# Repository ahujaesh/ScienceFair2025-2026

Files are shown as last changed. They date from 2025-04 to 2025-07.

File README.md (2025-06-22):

After placing third in the state and not advancing to ISEF, I wanted to build something that would allow me to make it there next year. What I came up with was this project: a DIY low cost bioprinter.

[BOM / Parts List](expenses.csv)

[Todo list / Agenda](plan.md) Note: (This will be replaced with a full instruction manual later, but as I am still iterating and changing the way I want to do this, I have included this file temporarily. This file is my thoughts on what the next steps for this project should be, and detailed info on what I am working on currently.)

[Media/Images](media) Images of the project will be uploaded here as they are taken.

What's happened so far?:

- Researched what bioprinting was to make sure it was the right fit for me  
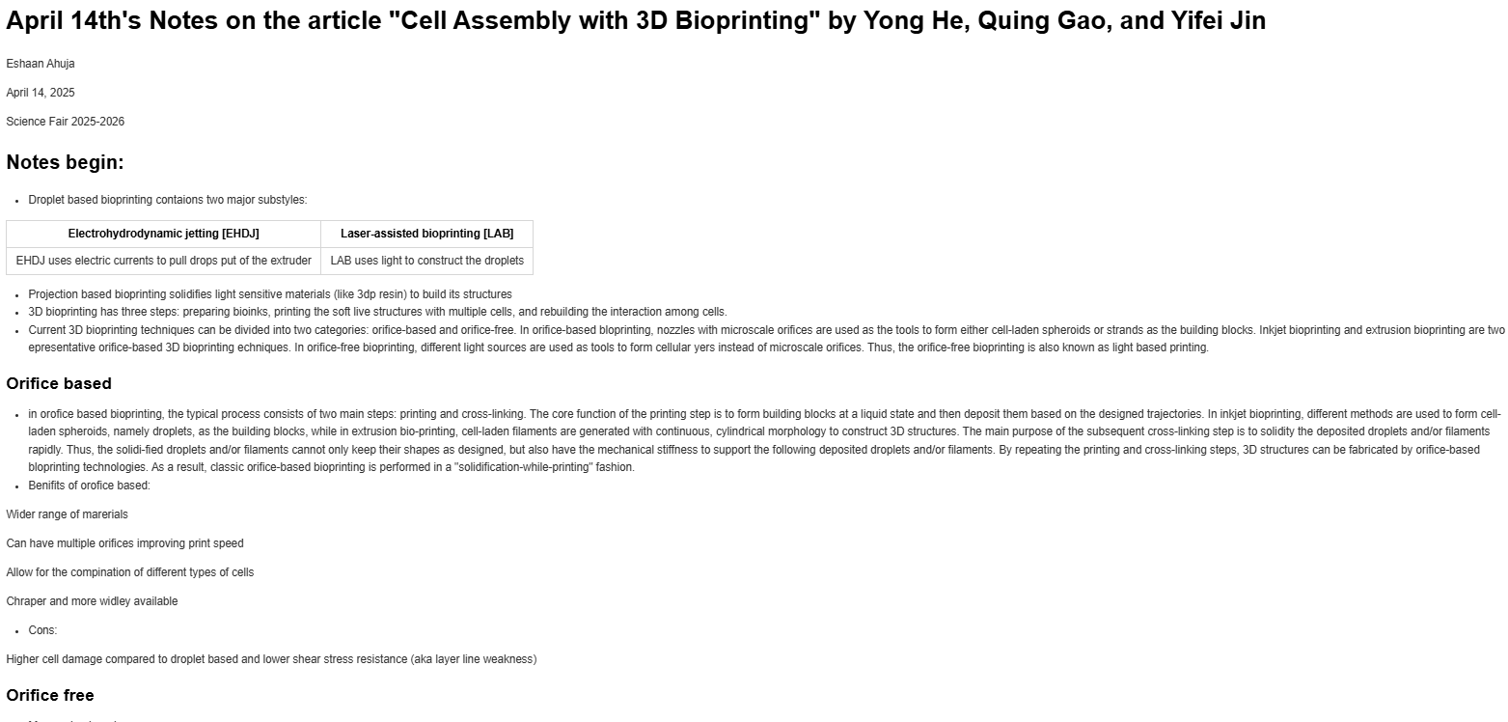
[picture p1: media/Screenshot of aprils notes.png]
Screenshot of notes

- Built an arduino mega based cardboard prototype of a bioprinter alongside a custom gcode interpreter and custom arduino OS  
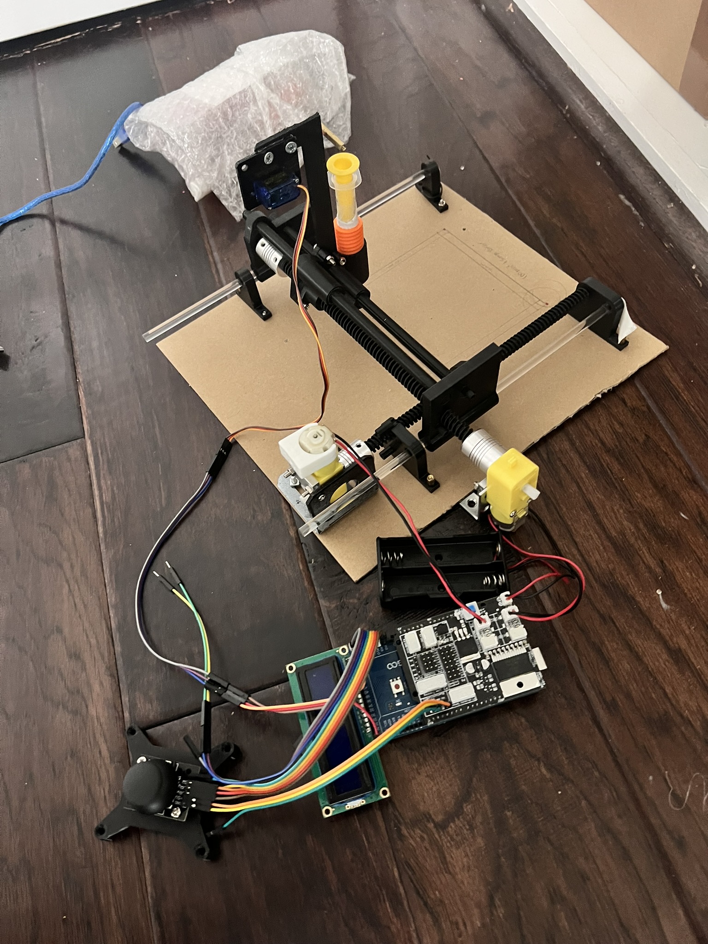
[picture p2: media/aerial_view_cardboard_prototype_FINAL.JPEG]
cardboard prototype

- Bought a used ender 3 pro and made a custom hotend mounting system, designed a custom paste extruder, modded the dimensions, installed a glass bed, and other mods; created a custom cura profile, made a klipper .cfg file, researched installation methods for klipper, made an agenda  
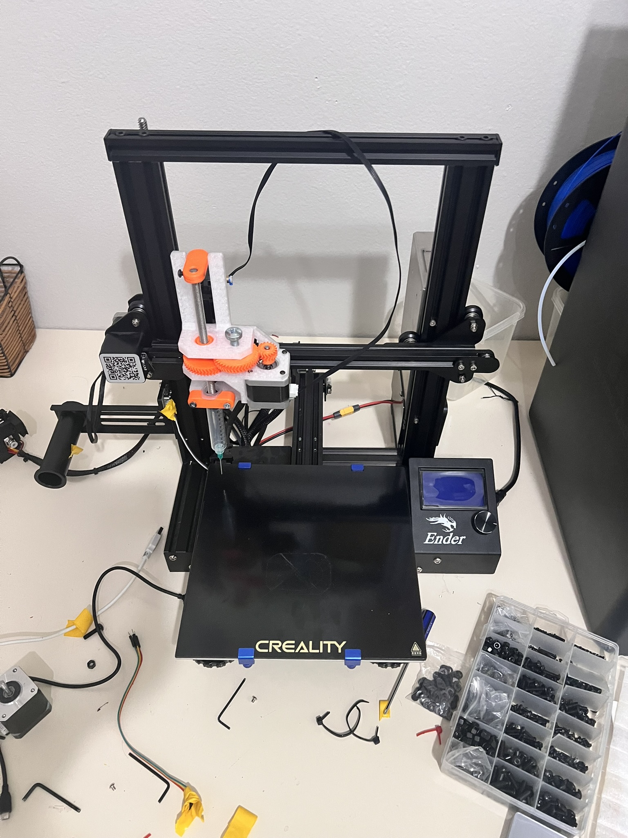
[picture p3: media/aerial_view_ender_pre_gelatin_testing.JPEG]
ender1


What's to come?:

- Complete modding the bioprinter
- Test the paste extruder with a gelatin and water mix; start tuning the print variables on this to not waste the more expensive final bioink
- Print with a bioink comprised of Chlorella Vulgaris (type of algae), Sodium Alginate (thickener, gives the consistency required to print the bioink), and Calcium Chloride (spray onto printed layers to make them stiff enough for the next layer to be printed on top). [Detailed Explanation for why this works](bioprinting/research/bioink.md)
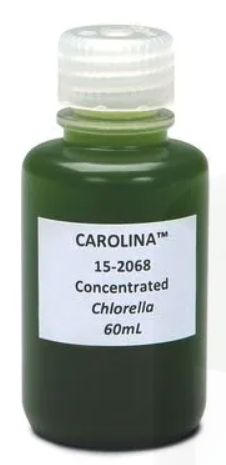
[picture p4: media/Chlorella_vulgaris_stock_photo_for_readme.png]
chlorella vulgaris stock photo

- Perhaps (not decided yet), print tissues with 3T3 cells (mouse) or HeLa cells (Human), if all previous steps are completed with enough time to allow for experimentation with more advanced cells.  
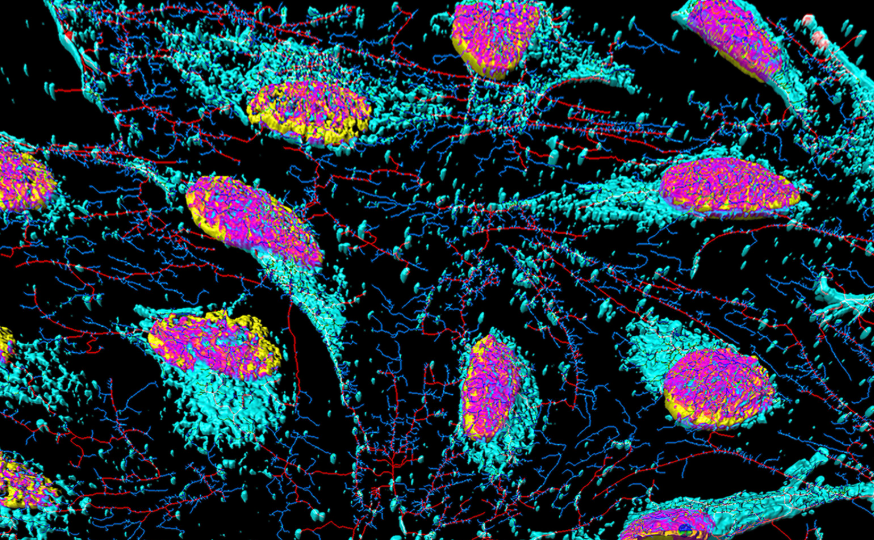
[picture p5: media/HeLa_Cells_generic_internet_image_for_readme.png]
HeLa generic internet image


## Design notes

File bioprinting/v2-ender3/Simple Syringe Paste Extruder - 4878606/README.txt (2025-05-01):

Simple Syringe Paste Extruder by craftworkstech on Thingiverse: https://www.thingiverse.com/thing:4878606

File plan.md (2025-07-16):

<h2>Project Timeline</h2>
<h3>Segment 1 - Complete</h3>
<div style="display: flex; align-items: center; justify-content: space-between; margin: 20px 0;">
  <div style="text-align: center;">
    
    <div><strong>1 - complete</strong><br><small>Research bioprinting and its feasibility</small></div>
  </div>
  
  <div style="text-align: center;">
    
    <div><strong>2 - complete</strong><br><small>Build a working <a href="media/aerial_view_cardboard_prototype_FINAL(1).JPEG">cardboard prototype</a></small></div>
  </div>
  
  <div style="text-align: center;">
    
    <div><strong>3 - complete</strong><br><small>Design and <a href="media/post_ender_mod_documentation (1).JPEG">build</a> a bioprinter based on an Ender 3 Pro</small></div>
  </div>
</div>
<h3>Segment 2</h3>
<div style="display: flex; align-items: center; justify-content: space-between; margin: 20px 0;">
  <div style="text-align: center;">
    
    <div><strong>4 - complete</strong><br><small>Install Klipper and perform a <a href="">dry run</a></small></div>
  </div>
  
  <div style="text-align: center;">
    
    <div><strong>5</strong><br><small>Print a cube out of gelatin to perform the majority of the tuning</small></div>
  </div>
  
  <div style="text-align: center;">
    
    <div><strong>6</strong><br><small>Print a leaf out of algae and test its ability to perform photosynthesis</small></div>
  </div>
</div>
<h3>Segment 3</h3>
<div style="display: flex; align-items: center; justify-content: space-between; margin: 20px 0;">
  <div style="text-align: center;">
    
    <div><strong>7</strong><br><small>Research the ISEF regulations on animal/human cells;<br> research if they could be printed on my printer and form a tissue</small></div>
  </div>
  
  <div style="text-align: center;">
    
    <div><strong>8a</strong><br><small>Print tissue out of 3T3 (mouse) cells and check for life</small></div>
  </div>
  
  <div style="text-align: center;">
    
    <div><strong>AND/OR 8b</strong><br><small>Print tissue out of HeLa (human) cells and check for life</small></div>
  </div>
</div>

Since my printer caught fire during my first attempt at getting a physical gcode running and burnt the extruder motor driver (Note: this is a great experience to talk about when judges want to hear about challenges during the ideation phase), I thought it would be a good idea to step back and look at where I want to go next.

<div style="display: flex; gap: 2%; justify-content: center; align-items: flex-start; margin-bottom: 24px;">
    <div style="flex: 0 0 25%; max-width: 25%; text-align: center;">
        <h5 style="margin-top: 0;">Burnt mobo</h3>
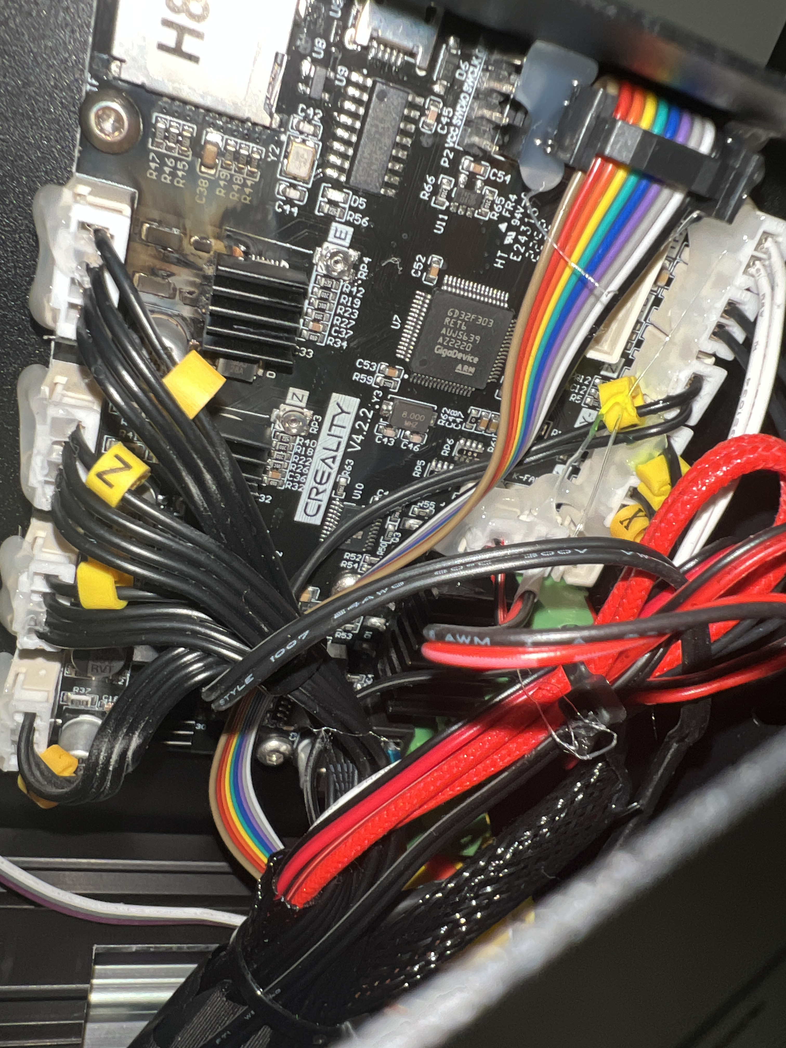
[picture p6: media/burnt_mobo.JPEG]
burnt mobo
        
    </div>
    <div style="flex: 0 0 25%; max-width: 25%; text-align: center;">
        <h5 style="margin-top: 0;">From left to right: mainsail on laptop, pi with external motor driver, bioprinter, paste extruder powered by external motor driver</h3>
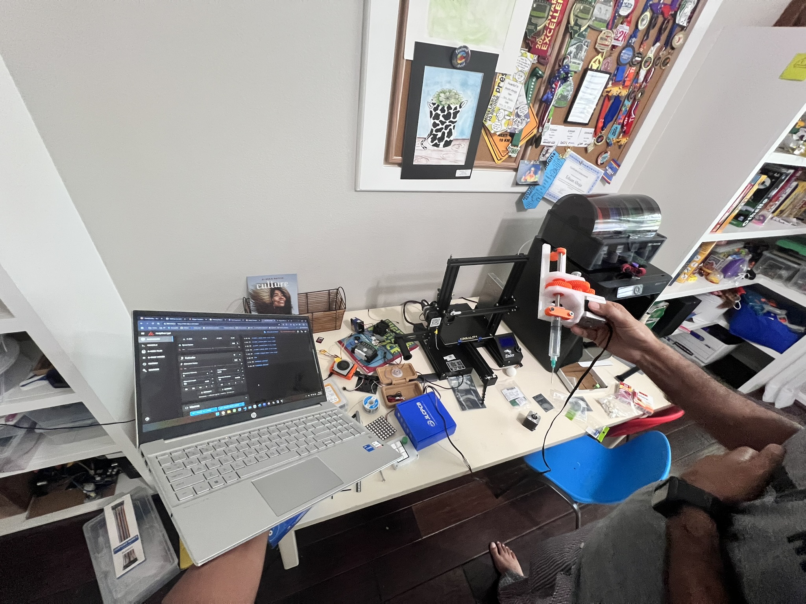
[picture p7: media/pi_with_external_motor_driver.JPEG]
aerial shot
        
    </div>
</div>

### What has been done so far:

Firstly, I removed whatever OS is currently loaded on the board's internal EEPROM and Memory (Which seems to be a version of Marlin, but which version I cannot be entirely sure of) and replaced it with a custom Klipper version, complete with proper cold extrusion support and allowing for the correct way to reverse the extruder motor, instead of the janky way that I tried to do it earlier, which resulted in the aforementioned fire. I then installed a build of Moonraker and Mainsail on the Raspberry Pi, flashed the Klipper file from that OS onto the modded Ender 3 Pro turned bioprinter, flashed another version onto the Raspberry Pi Zero, making two hosts for the Ender so that the signals intended for the burnt motor driver go through an external motor driver wired through the raspberry pi.

Todo list summary from the previous paragraph:

- [x] Install a build of Klipper, Moonraker and Mainsail
- [x] Add the printer .cfg file from below
- [x] Flash the Klipper .bin file from Mainsail OS onto the modded Ender 3 Pro turned bioprinter
- [x] Flash the Klipper .bin file from Mainsail OS onto the pi as the second mcu
- [ ] Start printing bioink!
- [ ] Finish all ECs, internships, etc.
- [x] Activate Github's Microsoft Azure free credit through the Student Developer pack for students 13-17
- [ ] Learn how to use Microsoft Azure
- [ ] Move the Vikunja instance to Microsoft Azure and reconnect it to the Cloudflare instance
- [ ] Move the Jellyfin instance into a docker container on the Synology DS212 2TB

Modifications to made to the Klipper profile from a stock Ender 3 Pro profile:

- [x] Cold extrusion
- [x] Change the Z height to account for the movement of the end stop to allocate for the increased size of the new toolhead
- [x] 0.8 mm nozzle size (the actual nozzle is 0.83mm in diameter, but the value of 0.8mm is easier for slicers to work with. I can tune out the difference through flow rate, line thickness, etc.) [CHANGED LINE 65]
- [x] Reverse the extruder motor [CHANGED LINE 61]
- [x] Change every movement (X, Y, and Z, not E) speed to max 5mm/s [completed in Cura]
- [x] Change extruder pins to rpi gpio pins
- [x] incl. mainsail cfg
- [x] pi as second mcu

Once I installed MainsailOS/Klipper on the Raspberry Pi of choice (see the .txt files in the "Klipper" directory), the plan to prevent another fire or severe accident would be to put the compiled Klipper OS for the printer on the SD card. This way, when I turn on the printer for the first time after the accident, the Klipper code will immediately replace the currently running marlin instance, preventing the execution of my accidentally malicious code that caused the fire because I will overwrite it before it has a chance to execute.

Before testing with material in the extruder, I first ran a ~30min dry run ([.gcode here](Klipper/cube_sliced_bioprinter.gcode); [Cura .3mf here](Klipper/cube_sliced_bioprinter.3mf)) to make sure that all motion axis and the klipper configuration were working well, before trying to actually print. In essence, I ran the print that I would have ran with gelatin without the gelatin to make sure everything worked before i added additional complexity. The only issue that I discovered was an error during the setup of the external motor driver, which was sending ~3.5 Amperes while the motor was expecting between 1 Ampere and 1.2 Amperes. After modifying the configuration of DIP switches on the rear of the unit, I was able to correct this error and proceed before any damage occurred to the motor. Besides this, the dry run went swimmingly, which puts us on track for gelatin testing once documentation is complete.

Once Klipper is running and the dry run is complete, the next step is testing with a gelatin and water mix. Before the fire, we saw that the printer successfully ran customized files, such as this [intestinal wall tissue](https://3d.nih.gov/entries/520) from the US National Library of Health, sliced in Cura, which, alongside a higher z endstop preventing the nozzle from crashing into the bed, would allow for testing with a gelatin and water mix to be able to happen immediately, if I fixed the issue of the extruder motor moving in the wrong direction. The reason the motor was moving in the wrong direction was that, during the installation of the M8 bolt that drives the central extrusion rod, I placed the bolt upside down in the slot due to a lack of consideration of the rod's movement direction. Due to this, the pole moved upwards during extrusion, a simple fix in Klipper but not so simple in the version of Marlin running on the bioprinter at the time. Now that I know that experimenting with Marlin settings instead of just biting the bullet and installing Klipper, a firmware that allows for much more customization, was the problem that led to the fire, I have gone ahead and written this file to prevent any more lapses in judgment from happening. Every significant step from here on out will be written in this document, allowing for better documentation and the prevention of logical errors that I could have avoided with more time spent contemplating the problem. Now that I have corrected the extrusion direction in the .cfg file, it is time to proceed to the next step: tuning the printer for printing a gelatin and water solution.

In theory, the printing of a gelatin and water solution is simple. Firstly, heat the solution of gelatin(~10g) and water (~50mL) till it reaches about $45\degree c$ (ideal extrusion temps are 35 to 45 $\degree c$), upon which it will transform into a gelatinous liquid that I can insert into the extruder by placing it below the orifice and reversing the extruder, effectively sucking up the liquid. While it is warm, I can extrude it like any other filament, and it will cool on the plate in ~30 seconds, allowing for the next layer to print on top. To prevent the cooling of the gelatin mix inside the syringe, I will add a solution later, but first, I would like to experiment with seeing how long the gelatin takes to cool; then, I can DIY a solution (such as an Arduino with a relay that heats a wire wrapped around the syringe, powered by a 12v battery, or a hairdryer mount that blows warm air onto the syringe without disturbing the print, possibly through a funnel or other system to direct the air current) and write it here. If it takes long enough to cool, it might be smarter to run small prints instead.

Now that I have went ahead and tested cooling, I am able to see that keeping the gelatin warm and liquid isn't the problem here, as it stays in liquid form for a few hours after formation; the actual problem is getting it to solidify enough for the next layer to be printed on top. Since a 4mm thick glass build surface is able to retain the temperatures from the freezer its been chilling in for up to 40 minutes, it is strategic to first chill the build plate, allow it to adjust to room temp during the startup of the printer, then print on the cold plate to allow for easy solidification of the first few layers. Since I aim to print tissue, which is not very thick, this should be an effective solution.

Any additional waste products or failed prints can be reheated into liquid form and reprinted, allowing for testing without wastage. The purpose of this step is to allow for tuning within a range of the actual bioink that will be used in the final product to prevent the waste of the final product for tuning purposes when you could use a $2.99 gelatin mix to tune instead. (Note: keep the temp below 60°C (140°F) to avoid breaking it down.)

### Gelatin Final Results

|Goal|What got printed|
|-|-|
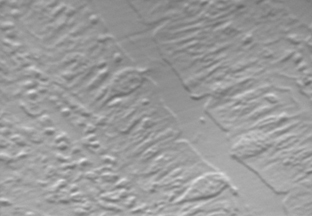
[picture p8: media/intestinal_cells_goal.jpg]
goal
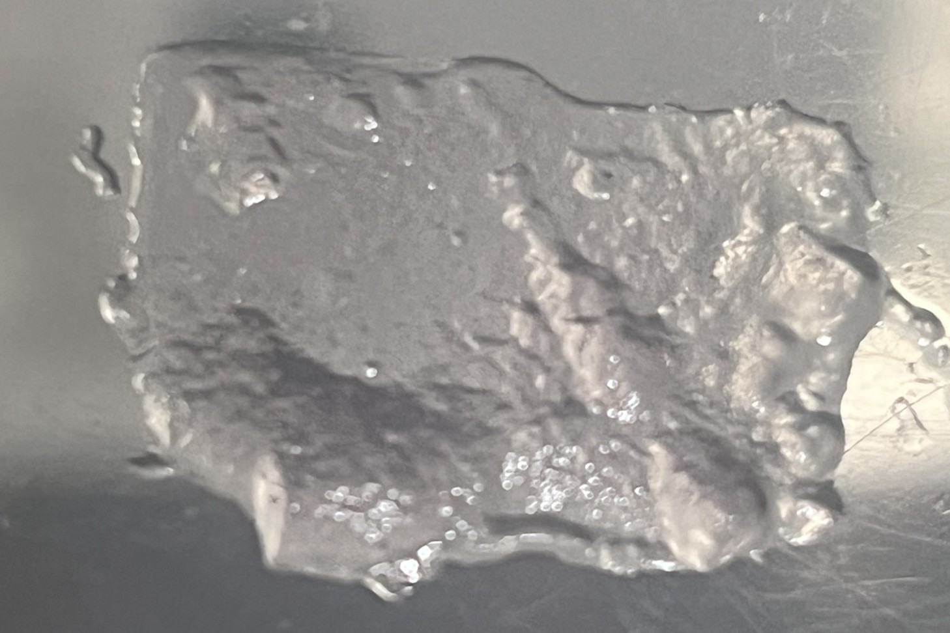
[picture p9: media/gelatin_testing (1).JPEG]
results
|||

Gelatin summary:

## All of the above has been done; everything below is to be done.

Additionally, I am also planning on making a full CAD design of the current bioprinter for use in renders and to aid in board creation.

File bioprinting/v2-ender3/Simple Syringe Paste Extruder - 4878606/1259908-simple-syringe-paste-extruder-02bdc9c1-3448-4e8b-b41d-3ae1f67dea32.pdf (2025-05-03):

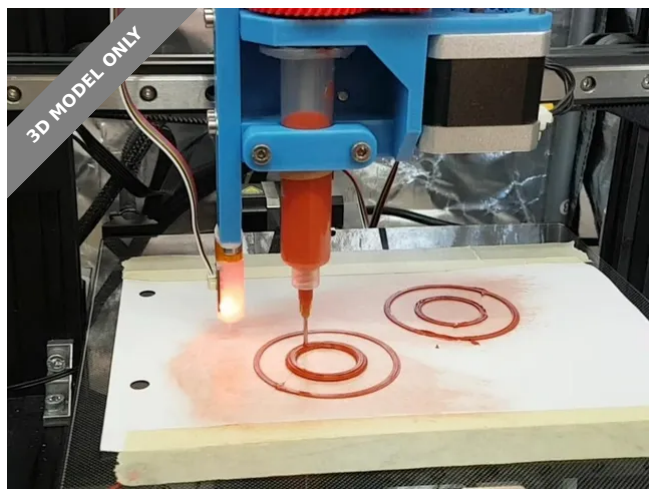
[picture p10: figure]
3D MODEL ONLY

## Summary

This is my first try realizing a syringe extruder.My first prototype worked surprisingly well but, this is still work...

3D Printers (https://printables.com/model?categoryId=1) > Other Printer Parts & Upgrades (https://printables.com/model?categoryId=2)

Tags: | extruder | syringe | paste | thingiverse | syringeextruder
pasteextruder

This is my first try realizing a syringe extruder. My first prototype worked surprisingly well but, this is still work in progress and more of quick and dirty rather than good engineering. I hope to make some updates/ upgrades but I do not make any promises. I designed it to fit on my Ender 3V2 with linear rail and dual z-axis mod and I wanted it easily removable so I went for the nice quick tool changer from @properprinting. There are many other designs for syringe extruders available, some quite good, but I wanted to use not parts, that I didn't already have (syringes, screws and bearings) and fit easily to the printer and tool changer (e.g. I used three gears instead of one very big and one very small).

I included all STEP files, so feel free to modify for your needs.

craftworks.tech (https://printables.com/@sr6imp_108358)

## Simple Syringe Paste Extruder

VIEW IN BROWSER (https://printables.com/model/1259908-simple-syringe-paste-extruder)

updated 9. 4. 2025 | published 9. 4. 2025

Materials for printing:

I wanted to be able to print silicone for some uses at work and try some other things like chocolate (yet to come, including heating/cooling), but you can print many paste-like substances, preferably thixotropic, not too viscous but not too liquid either. Nutella would work good I think but unfortunately it does not solidify. I used RTV 159 silicone (thixotropic high temperature) for a kitchen sink gasket and it worked quite well.

For 'runny' liquids you can use the extruder as a dispenser.
Required settings:E-steps/flow:

The gear ratio is 2x 1:2.5 so combined 1:6.25. The rotational to linear conversion is done by a standard M8 nut and M8 rod (with 1.25mm pitch). The force you need and the e-steps / flow is mainly dependent on the viscosity of your material and the size of your tip. I estimated that I needed cranking up my e-steps to 500 (from 93 with a stock Ender 3v2 or in my case 140 with dual gear extruder) and it worked pretty well, slight flow adjustments should be sufficient.
Temperature:

I disabled the heated bed (0°C) and had to enable Cold Extrusion by using the M302 P1 command (and M500 for storing, remember to disable with M302 P0 afterwards).
Print speed:

I used 20mm/s, worked very well, i guess you can go a lot faster, depending on the material you print. But mind not only the possible extrusion flow but also the weight of the extruder. Single-z-axis-motor systems like stock Ender 3 or 3v2 may have also issues with the weight.
Retraction:

I designed the mechanism incl. plunger fixation to make retraction possible. Especially for materials with low viscosity that's a must in my opinion. The value depends on the material and tip size. Just try.
Z-seam:

I had some inconsistencies at the z-seam, i guess you can improve a lot using combing.

Bed type:

Dependent on your material. For silicone i taped a sheet of paper on the glass bed, worked good, especially after a failed print when you rub it off and print again. I thought (ptfe-coated) permanent baking paper would also be a good option.
Nozzle position:

The nozzle in this design is about 25mm to the left and 6mm to the front, compared to a generic Ender 3v2, but just for the nozzle. With the tool changer (and in my case the linear x-axis) it is some 20mm more in y direction, so I lose a little bit printing area. I like to address it if I have time, but for now the print area is more than sufficient.
Parts needed:

I designed this extruder for parts i already had, so I didn't spent time on thinking where and what to get. You will need 1x M8 threaded rod. length dependent on your syringe, should be ~50mm longer. I used 180mm. 3x ball bearings 608zz (for the gears). I guess you could even use 3d printed bearings such as https://www.thingiverse.com/thing:4851975 4x M4x5 or M4x6 set screws (for the axle fixations) 1x M8x25, x30 or x35 (for the middle gear), you could also use a bit of M8 rod. 4x M5x10 (for the Quick Tool Adapter) 8x M3x10 or similar (for the motor and BLTouch mount) 4x big M3 washers (for the BLTouch mount) 3x M3x6 or similar (for the NORDSON plunger and BLTouch) For the motor you can use any standard NEMA17 motor, either the extruder motor from your printer (e.g. Ender 3) or a new one (like i did to reduce tool changing effort) NORDSON EFD 10ccm syringes/'barrels' (e.g. 7012007) , plungers/'pistons' (e.g. 701224) and nozzles/'tip' (e.g. 7018106) or compatible. You can get all 3D-models here: https://www.3dcontentcentral.com/parts/supplier/EFD,-Inc.aspx, I don't include them because I don't know the copyright situation.
BLTouch:

I added an adjustable BLTouch mount, for easy homing. No need to use it, but I like it very much.
Notes on threads:

I like printed threads, even in PLA. If your printer is tuned correctly and the treads are well designed (size and legth) printed threads should work fine for most applications. If you have print issues you can always use a tap cutter. For threads used very often you can modify it to use thread inserts or nuts.

Notes on Quick Tool Changer:

Modified quick tool holder for this extruder: https://www.thingiverse.com/thing:4878149 (https://www.thingiverse.com/thing:4878149) @properprinting's Quick change tool system: https://www.thingiverse.com/thing:3369444
Known issues:

I had some trouble that the syringe was pushed out because the grip wasn't good enough. So I put a small piece of sand paper in between. For V1.1. I added a holder (just turn the syringe 90°) so this shouldn't be an issue any more.
assembling/disassembling of the plunger is a bit tricky, I want to improve that, maybe using set screws and I want to add a variant for a rubber type plunger.
Changes V1.1:

added a missing hole
added a hole for the tool changer lever screw
added a holder to keep the syringe from being pushed out
added a hexagon to the plunger adapter for easier installation / removal
made the holes for the tool changer adapter slightly bigger Print Settings

Printer Brand:

Creality

Printer:

Ender 3

Rafts:

No

Supports:

No

Resolution:

0.2

Infill:

•

•

•
•
•
•

•

## Model files

20

Filament: Amazon Basic PLA blue, red Notes:

Print 4 or 5 wall lines for strength, much more important than infill. PTEG might be even better, but PLA is more than sufficient.

No supports needed - two gears have a sacrificial layers, just cut away after printing.

Category: 3D Printer Extruders

body.stl

clamp.stl

guide.stl

plunger_mount.stl

gear_motor_18teeth.stl

gear_rod_42teeth.stl

Find source .stl files on Thingiverse.com (https://www.thingiverse.com/thing:4878606)

## License

This work is licensed under a
Creative Commons (4.0 International License)

Attribution-ShareAlike (http://creativecommons.org/licenses/by-sa/4.0/)

✖ | Sharing without ATTRIBUTION
✔ | Remix Culture allowed
✔ | Commercial Use
✔ | Free Cultural Works
✔ | Meets Open Definition

gear_middle_42-18teeth.stl

blt_holder.stl

syringe_extruder.step

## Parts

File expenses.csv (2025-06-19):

Product | Purpose - Short | Approx cost | Purpose - Long | Possible Buying locations
Sodium Alginate | bioink base | $10/4oz | Suspend cellsin this material to print in jelly, converts to solid after reaction with calium chloride | Food grade sodium alginate on amazon, mixed with water & cells to create a bioink that is sterile enough for my purposes (not lab grade but good enough) https://www.amazon.com/Ingredient-Thickening-Molecular-Gastronomy-Component/dp/B09MWQ45Z9?adgrpid=1331509142862881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
Calcium Chloride (CaCl₂) | Solidifies bioink base | $8/2oz | once the first layer is printed, this is sprayed on to allow the next layer to be printed on top | Food grade CaCl₂ on amazon, sterile enough for my purposes (not lab grade but good enough) https://www.amazon.com/Calcium-Chloride-Molecular-Gastronomy-Certified/dp/B00BLPNJLK
used ender 3 pro | base structure for modding | $80
glass print bed | hold printed component - bought with the used ender 3 pro for $0 | $0
filament (PLA, PETG, ABS, PC) | custom designed parts | $40 | printed on a bambu lab p1sc - some (PLA, PETG) bought with the used ender 3 pro - others (PC, ABS) from microcenter
Gelatin | low cost testing material for use before lab grade material to confirm printer function | $2.99 |  | bought from target
Cells | living part | $15 |  | carolina biological supply https://www.carolina.com/algae/auxenochlorella-chlorella-pyrenoidosa-living/152067.pr?question=algae
Pi | control system | $80 |  | bought from microcenter
pi fan | used to cool the pi | $0 |  | scrapped from an old toshiba
pi case | 3d printed in pla with open source design, used to protect the pi from damage | $0 |  | bambu p1sc
stepper | for syringe, replaces the extruder stepper as it isn't being moved just unplugged |  |  | bought from microcenter
printed parts for the mod kit | this kit allows for a syringe instead of a extruder |  |  | bambu p1sc
klipper with pi as mcu | software |  |  | internet/Klipper3D
screws and bolt m3-m8 | misc - bought one big kit fromm amazon | $20 |  | bought from amazon
stepper wires | the steppers from microcenter didn’t come with wires |  |  | bought from microcenter
syringe with needle |  |  |  | bought from amazon
laptop | used for headless pi | $0 | exempt from cost | N/A

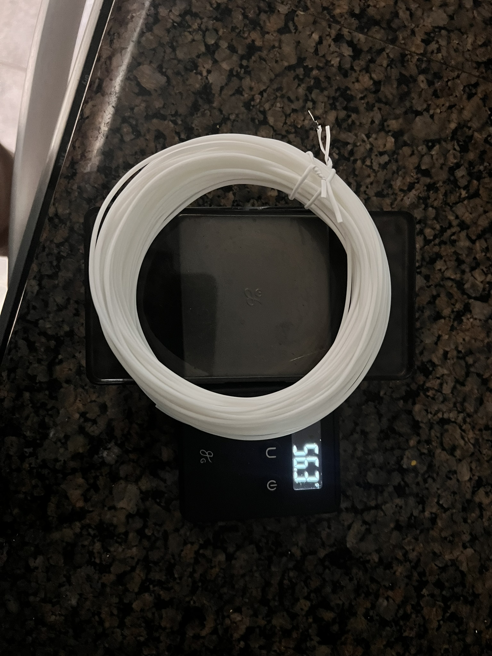
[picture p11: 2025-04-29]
media/measuring_pla_from_first_purchase(1).JPEG

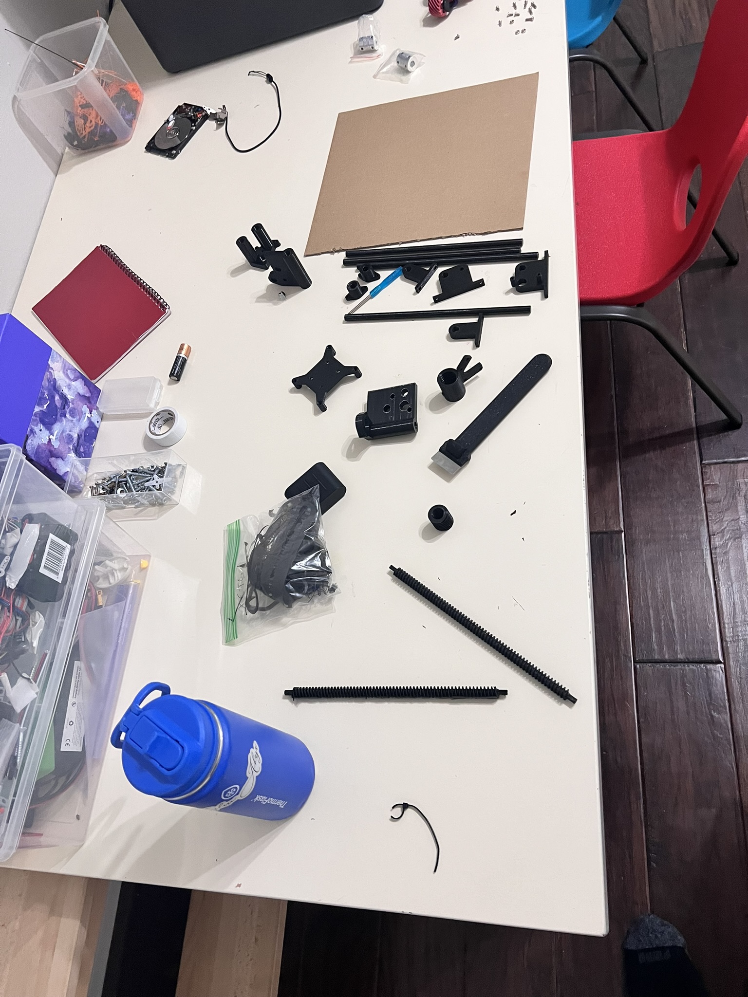
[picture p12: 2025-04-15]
media/first_3d_print_job_parts_pre_assembly.jpeg

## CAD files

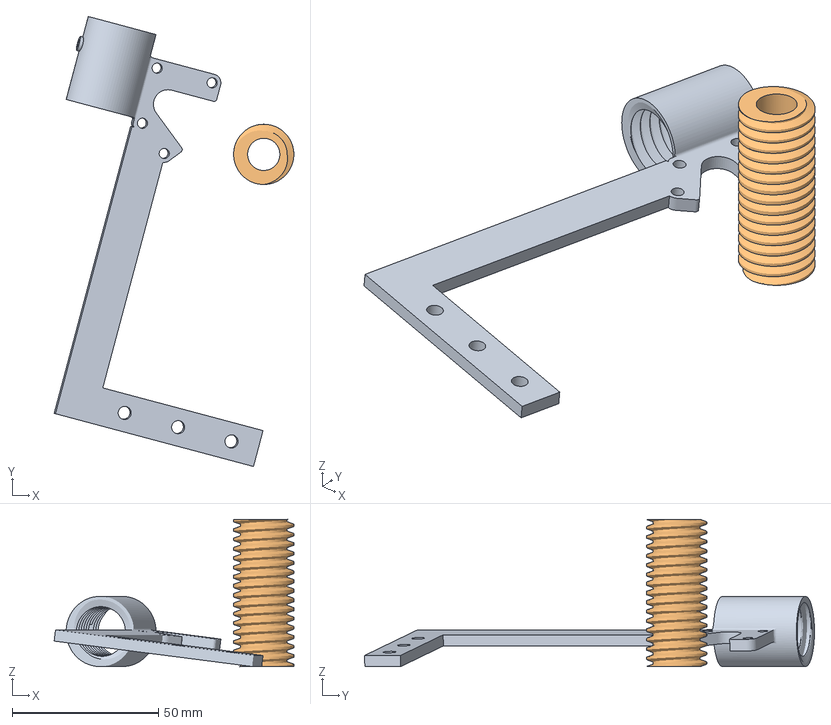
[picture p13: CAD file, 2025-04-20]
bioprinting/v1-2dPlotter/pen_holder2v3.3mf
82.0 x 153.9 x 50.3 mm
pen_holder2v3.stl
pen_holder2v2.stl

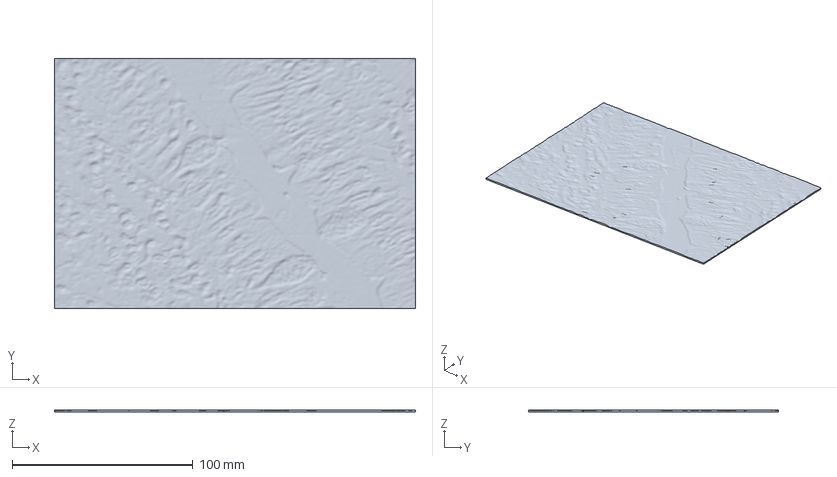
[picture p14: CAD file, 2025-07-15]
bioprinting/v2-ender3/intestinal_wall_tissue.3mf
200.0 x 138.4 x 1.38 mm

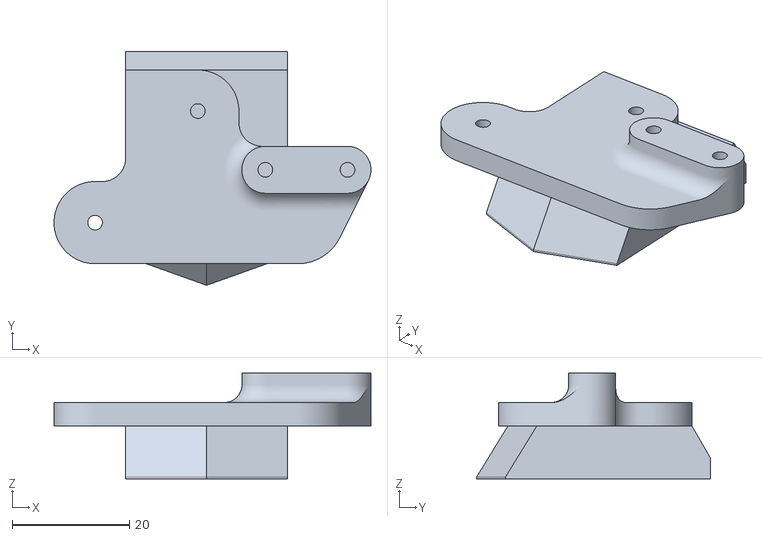
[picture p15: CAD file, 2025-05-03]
bioprinting/v2-ender3/Quick-tool-change/Hot_end_holder_og.stl
54.0 x 39.8 x 18.0

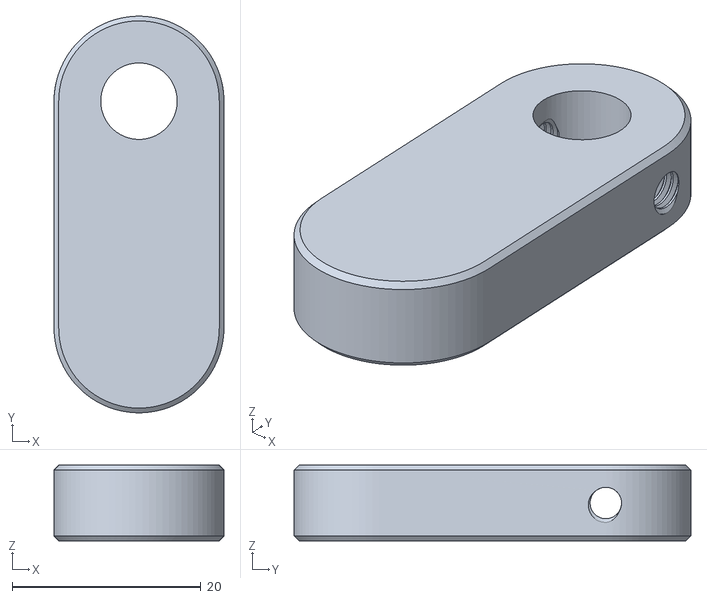
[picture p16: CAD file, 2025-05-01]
bioprinting/v2-ender3/Simple Syringe Paste Extruder - 4878606/files/Guide.stl
18.0 x 42.0 x 8.00

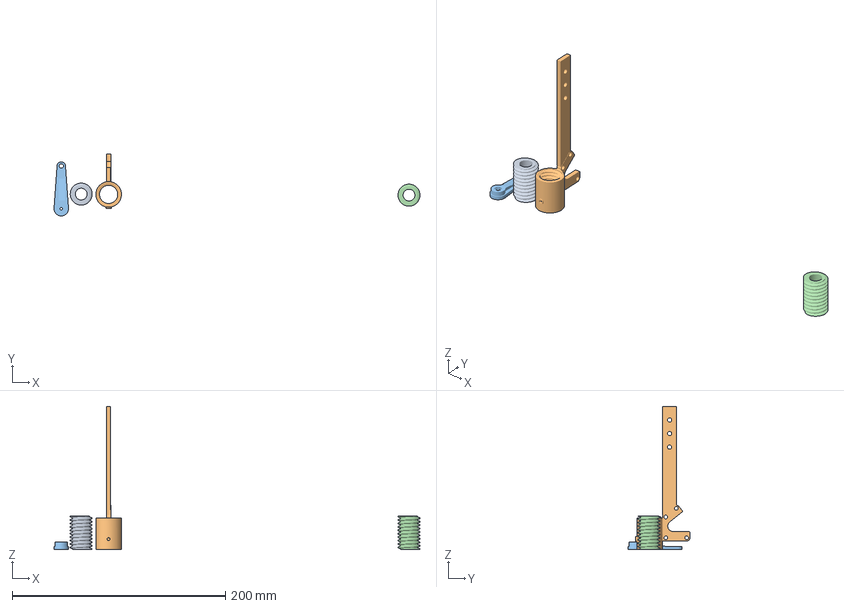
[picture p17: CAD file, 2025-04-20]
bioprinting/v1-2dPlotter/pen_holder2.3mf
343.0 x 58.0 x 134.1 mm
Assembly x 2
pen_holder2v2.stl
Custom Servo Horn2.stl

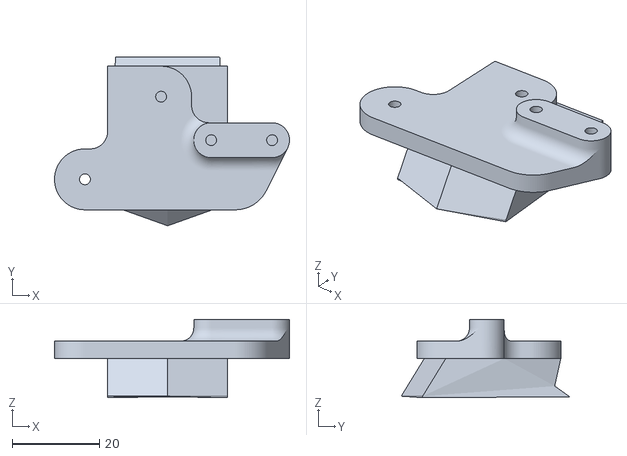
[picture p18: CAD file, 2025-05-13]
bioprinting/v2-ender3/hot_end_holder_og_redesigned_v2.stl
54.0 x 38.7 x 18.0

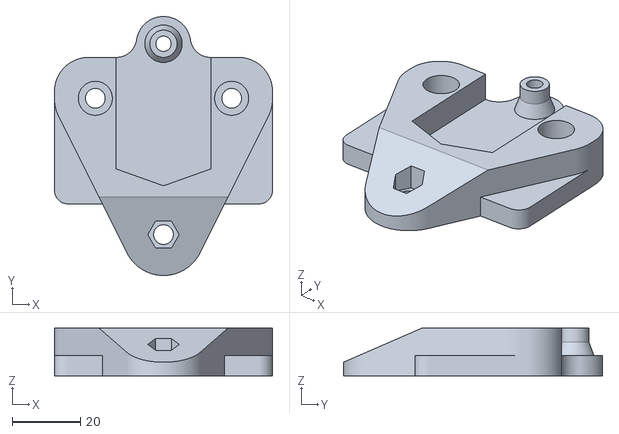
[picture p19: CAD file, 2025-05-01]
bioprinting/v2-ender3/Quick-tool-change/Quick tool change base V5.stl
64.0 x 76.0 x 14.0

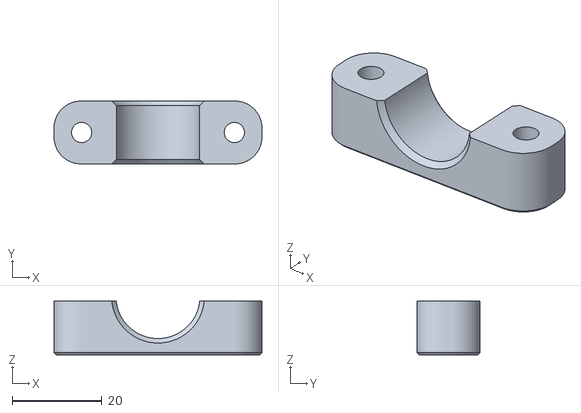
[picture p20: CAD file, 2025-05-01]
bioprinting/v2-ender3/Simple Syringe Paste Extruder - 4878606/files/Clamp.stl
46.3 x 14.0 x 12.0

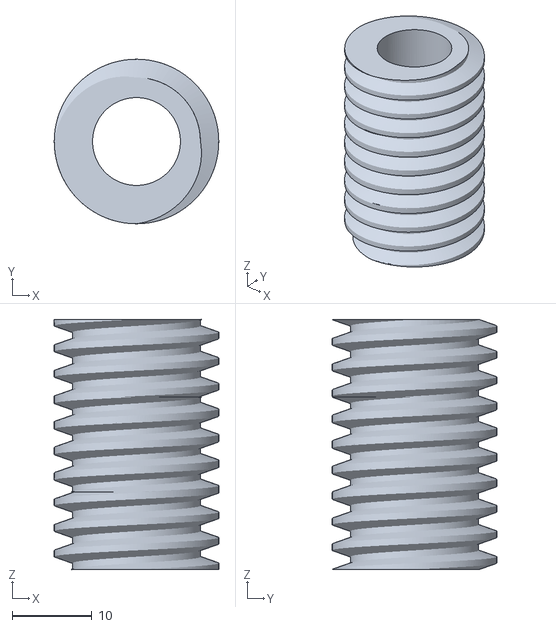
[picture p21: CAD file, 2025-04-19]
bioprinting/v1-2dPlotter/pen_holder2v2.stl
20.6 x 20.6 x 31.3

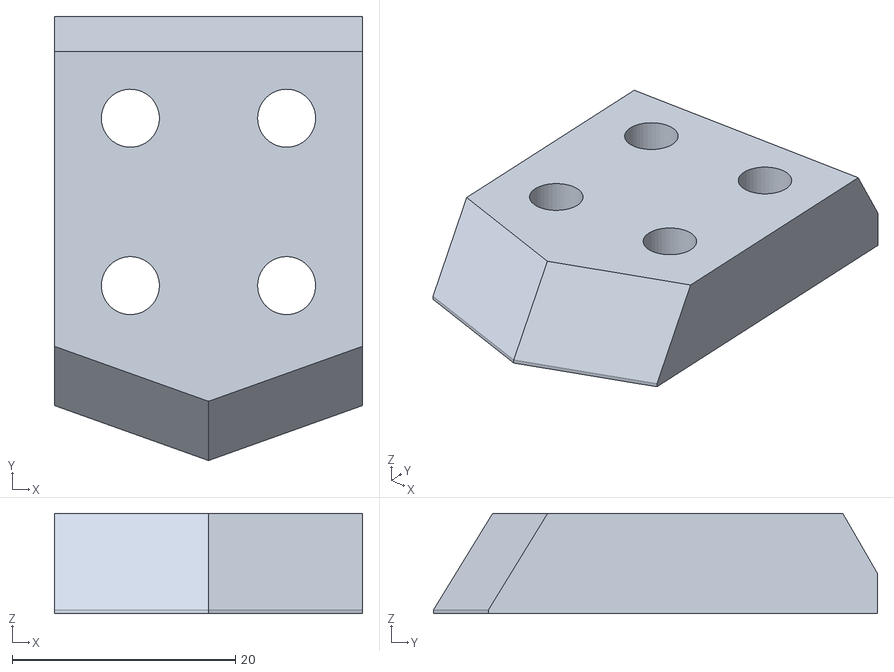
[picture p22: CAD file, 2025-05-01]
bioprinting/v2-ender3/Quick-tool-change/Hot_end_holder.stl
27.6 x 39.8 x 9.00

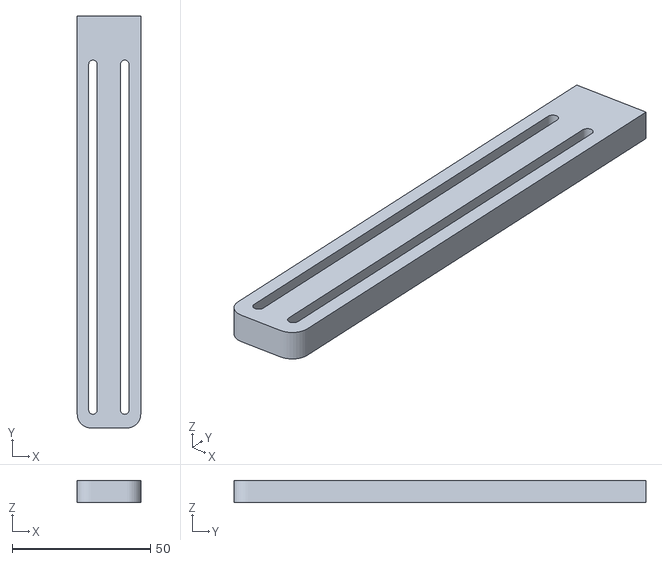
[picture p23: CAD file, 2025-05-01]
bioprinting/v2-ender3/Simple Syringe Paste Extruder - 4878606/files/BLT_Holder.stl
23.0 x 149.0 x 8.00

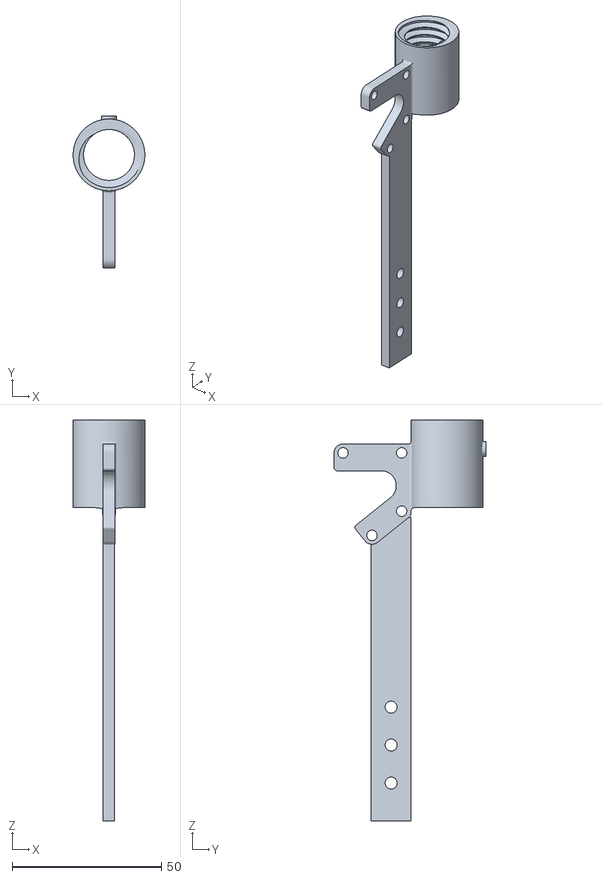
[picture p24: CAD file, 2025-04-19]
bioprinting/v1-2dPlotter/pen_holder1v2.stl
24.0 x 50.8 x 134.1

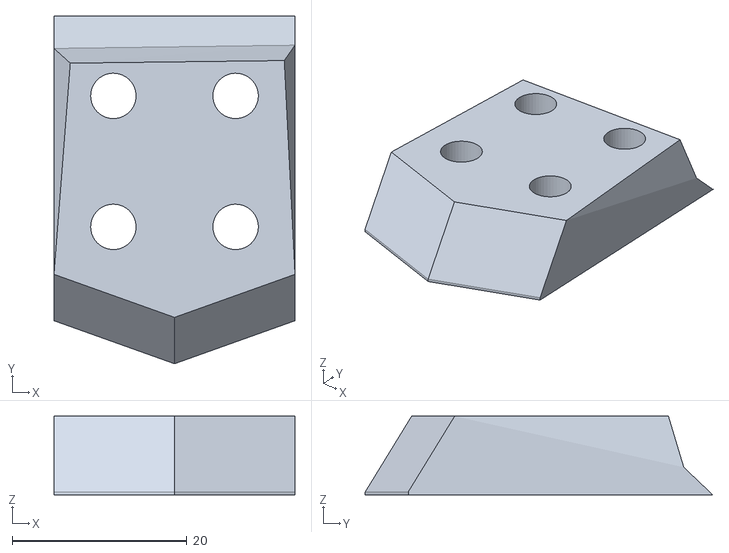
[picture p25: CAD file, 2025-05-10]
bioprinting/v2-ender3/hot_end_holder_redesigned.stl
27.6 x 39.8 x 9.00

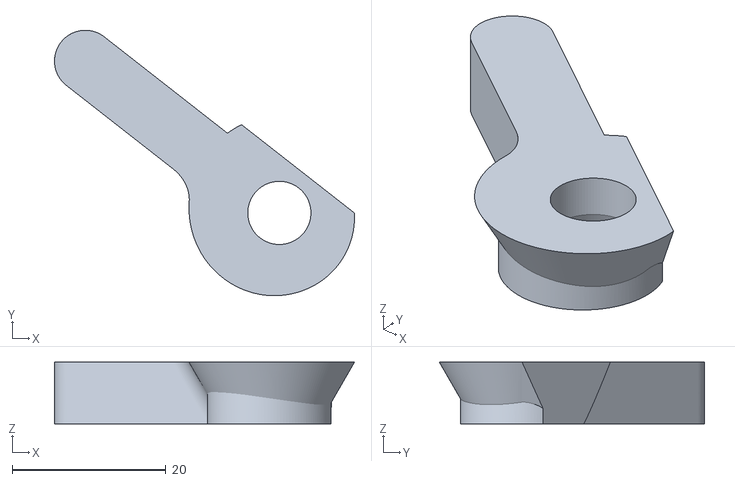
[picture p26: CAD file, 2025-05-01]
bioprinting/v2-ender3/Quick-tool-change/Lever.stl
39.0 x 34.5 x 8.00

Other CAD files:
bioprinting/v2-ender3/hot_end_holder_og_redesigned.stl
bioprinting/v2-ender3/Simple Syringe Paste Extruder - 4878606/files/Body.stl
bioprinting/v1-2dPlotter/Custom Servo Horn.stl
bioprinting/v1-2dPlotter/Custom Servo Horn2.stl
bioprinting/v1-2dPlotter/footer.stl
bioprinting/v1-2dPlotter/footer2.stl
bioprinting/v1-2dPlotter/footer4.stl
bioprinting/v1-2dPlotter/pen_holder1.stl
bioprinting/v1-2dPlotter/pen_holder2.stl
bioprinting/v1-2dPlotter/pen_holder2v3.stl
bioprinting/v1-2dPlotter/slider1.stl
bioprinting/v1-2dPlotter/slider3.stl
bioprinting/v1-2dPlotter/slider4.stl
bioprinting/v1-2dPlotter/standoff.stl
bioprinting/v1-2dPlotter/worm_gear_2.stl
bioprinting/v2-ender3/1xM3x10mmThreadedRod.3mf
bioprinting/v2-ender3/1xM3x8mmThreadedRod.3mf
bioprinting/v2-ender3/1xM4x6mmThreadedRod.3mf
bioprinting/v2-ender3/1xM5x10mmThreadedRod.3mf
bioprinting/v2-ender3/1xM8x35mmThreadedRod.3mf
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

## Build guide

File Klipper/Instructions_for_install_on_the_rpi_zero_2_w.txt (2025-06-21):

Just use the standard install provided my mainsailOS, since there is no OS to preserve, unlike the rpi5, which is currently in use and cannot have its os changed due to a loss of data. Link: https://docs-os.mainsail.xyz/getting-started/raspberry-pi-os-based

Once everything is installed, continue with the plan.

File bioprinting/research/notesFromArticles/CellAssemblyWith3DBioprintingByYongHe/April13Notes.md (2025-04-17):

# April 13th's Notes on the article "Cell Assembly with 3D Bioprinting" by Yong He, Quing Gao, and Yifei Jin

Eshaan Ahuja

April 13, 2025

Science Fair 2025-2026

|Outline of current Idea|
|-|
|The current thought process (prior to any reading of literature on the subject), is to build a modified 2D plotter running on an Arduino Mega and Motor Control Board to allow for the attachment of an extrusion device to eject living simple cells suspended in bioink to form tissues. The Arduino Mega's main movement system is currently being thought of as joystick controlled, with manual movements creating the two dimensional figures in separate petri dishes, and the stacking of layers afterwards allows for the creation of the finished tissue. The goal would be to also modify it to run on a traditional 3D printer software, and allow for the processing of G-Code, allowing for more complex shapes than a manual machine could perform. As of this moment, the Arduino Mega has been configured to run off of a joystick movement system, which would power the rudimentary 2D plotter currently printing in PETG on my Bambu P1S Combo, an 11 hour overnight print.|

|Goal for this note taking session|
|-|
|Identify the feasibility of the creation of these cells and bioinks at the current level of skill, and understand conceptual mechanics of the subject, filling in misconceptions about how the attachment and creation of layers would work, and if this project could work. Alongside this, another goal would be to identify the type of cell that would most accurately fulfill my goal of forming tissues while still conforming to ISEF rules on cells and my current abilities. The article that will be read today, "Cell Assembly with 3D Bioprinting" by Yong He, Quing Gao, and Yifei Jin, is an article establishing various methods of utilizing this cutting edge technology, and should allow me to meet my goals for research tonight. While it was written in 2021, four years before this project started, and quite behind given that this concept of bioprinting has been around for such a short time, it should me modern enough for my purposes.|

## Notes Begin:

- Bioprinting was first demonstrated in 1988 when a standard HP inkjet printer was modified to be able to deposit cells.

- 3D bioprinting has three main categories:

|Extrusion Based|Droplet Based|Projection Based|
|-|-|-|
|Extrusion based generates structures similar to how a standard FDM printer works, with continuous fibers. This is the most commonly used method|Droplet Based works similar to the blob printing style of FDM ([Eg.](https://fullcontrol.xyz/#/models/800020))|Projection Based works similar to standard resin 3D printers, utilizing the photosensitive properties of materials to form layers|

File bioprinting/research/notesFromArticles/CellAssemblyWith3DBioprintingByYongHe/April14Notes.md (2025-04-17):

# April 14th's Notes on the article "Cell Assembly with 3D Bioprinting" by Yong He, Quing Gao, and Yifei Jin

Eshaan Ahuja

April 14, 2025

Science Fair 2025-2026

## Notes begin:

- Droplet based bioprinting contains two major substyles:

|Electrohydrodynamic jetting [EHDJ]|Laser-assisted bioprinting [LAB]|
|-|-|
|EHDJ uses electric currents to pull drops put of the extruder|LAB uses light to construct the droplets|

- Projection based bioprinting solidifies light sensitive materials (like 3dp resin) to build its structures

- 3D bioprinting has three steps: preparing bioinks, printing the soft live structures with multiple cells, and rebuilding the interaction among cells.

- Current 3D bioprinting techniques can be divided into two categories: orifice-based and orifice-free. In orifice-based bloprinting, nozzles with microscale orifices are used as the tools to form either cell-laden spheroids or strands as the building blocks. Inkjet bioprinting and extrusion bioprinting are two representative orifice-based 3D bioprinting techniques. In orifice-free bioprinting, different light sources are used as tools to form cellular layers instead of microscale orifices. Thus, the orifice-free bioprinting is also known as light based printing.

### Orifice based

- In orifice based bioprinting, the typical process consists of two main steps: printing and cross-linking. The core function of the printing step is to form building blocks at a liquid state and then deposit them based on the designed trajectories. In inkjet bioprinting, different methods are used to form cell-laden spheroids, namely droplets, as the building blocks, while in extrusion bio-printing, cell-laden filaments are generated with continuous, cylindrical morphology to construct 3D structures. The main purpose of the subsequent cross-linking step is to solidity the deposited droplets and/or filaments rapidly. Thus, the solidified droplets and/or filaments cannot only keep their shapes as designed, but also have the mechanical stiffness to support the following deposited droplets and/or filaments. By repeating the printing and cross-linking steps, 3D structures can be fabricated by orifice-based bloprinting technologies. As a result, classic orifice-based bioprinting is performed in a "solidification-while-printing" fashion.

- Benefits of orifice based:

Wider range of materials

Can have multiple orifices improving print speed

Allow for the combination of different types of cells

Cheaper and more widely available

- Cons:

Higher cell damage compared to droplet based and lower shear stress resistance (aka layer line weakness)

### Orifice free

- Many subcategories:

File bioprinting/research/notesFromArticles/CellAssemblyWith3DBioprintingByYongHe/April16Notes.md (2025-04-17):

# April 16th's Notes on the article "Cell Assembly with 3D Bioprinting" by Yong He, Quing Gao, and Yifei Jin

Eshaan Ahuja

April 16, 2025

Science Fair 2025-2026

## Notes  [Cont. april 14]:

### Orifice Free:

Pros:

Cons:

Expensive

Takes a while to create the machine

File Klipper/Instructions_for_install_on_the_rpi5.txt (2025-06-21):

Since the OS is to be preserved on this rpi, the plan is to install klipper without installing a new OS, unlike the rpi zero 2 w, upon which i can install a new os, since there is no data to be preserved.

Instructions:

Use KIaUH to install everything instead of having it preinstalled on an OS (git clone https://github.com/th33xitus/kiauh.git ~/kiauh && ~/kiauh/kiauh.sh)

Once everything is installed, continue with the plan.

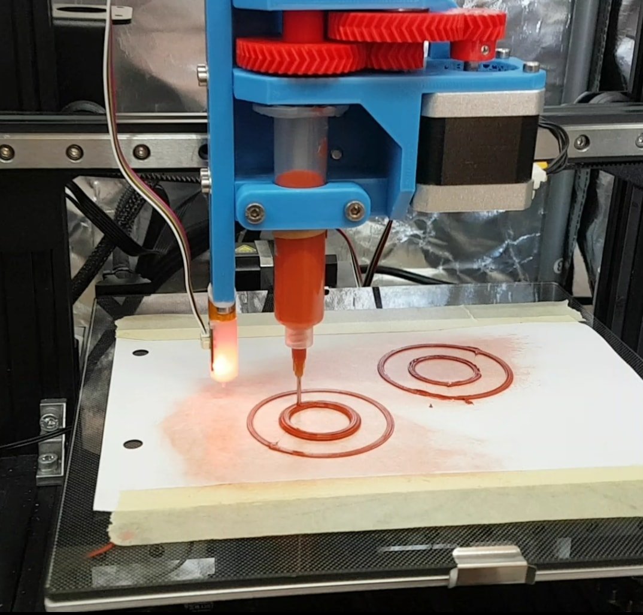
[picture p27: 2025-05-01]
bioprinting/v2-ender3/Simple Syringe Paste Extruder - 4878606/images/Printing.jpg

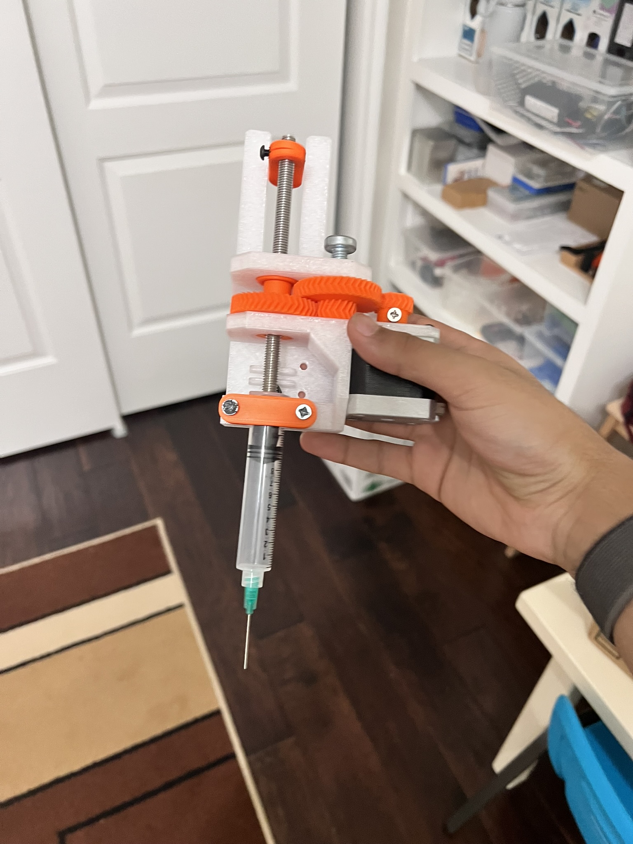
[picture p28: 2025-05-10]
media/finishedassemblyv1.JPEG

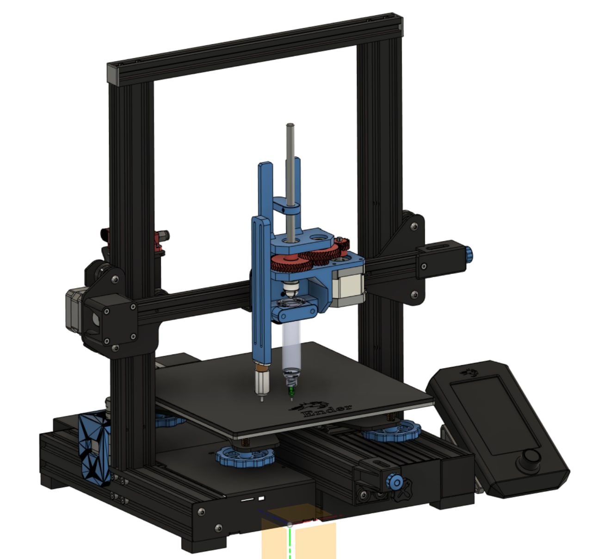
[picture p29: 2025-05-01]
bioprinting/v2-ender3/Simple Syringe Paste Extruder - 4878606/images/Printer.jpg

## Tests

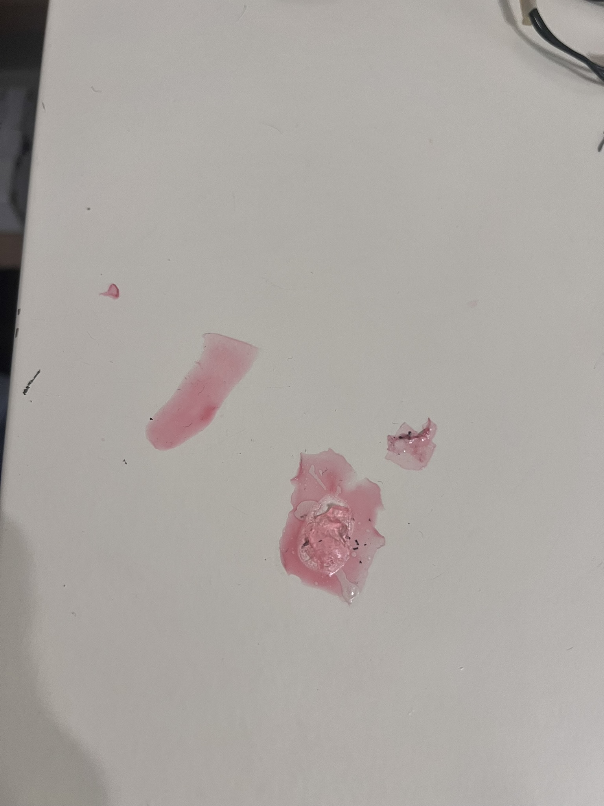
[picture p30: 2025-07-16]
media/gelatin_testing (9).JPEG

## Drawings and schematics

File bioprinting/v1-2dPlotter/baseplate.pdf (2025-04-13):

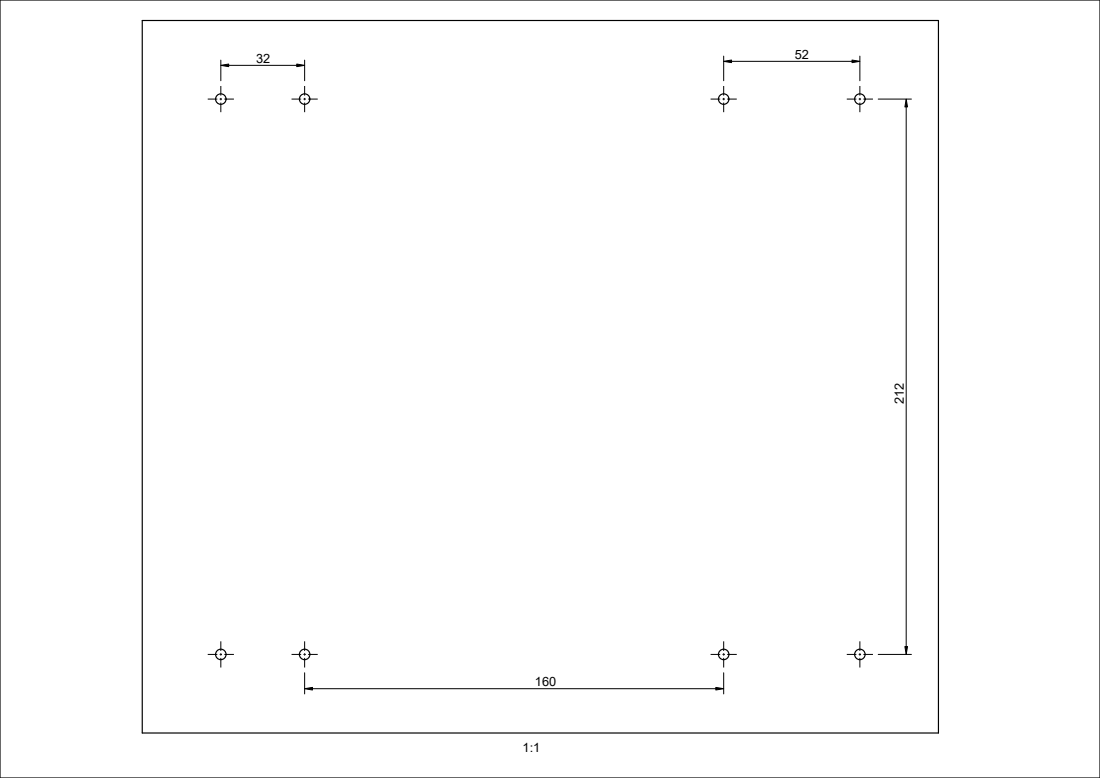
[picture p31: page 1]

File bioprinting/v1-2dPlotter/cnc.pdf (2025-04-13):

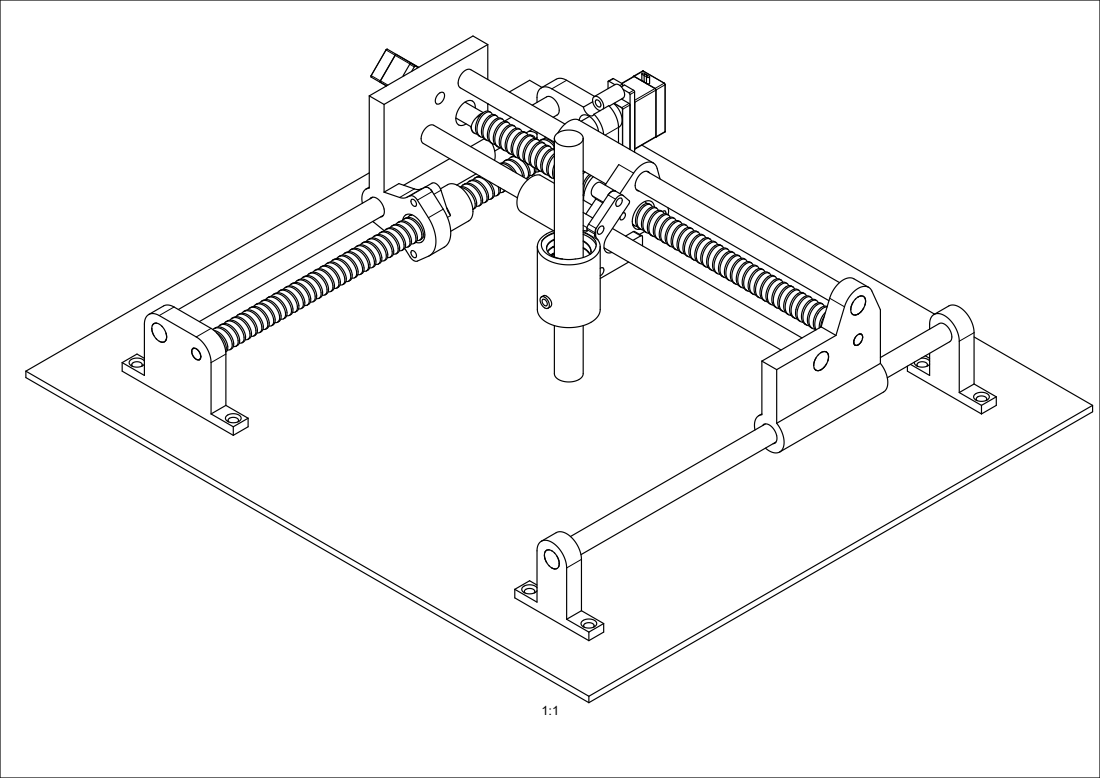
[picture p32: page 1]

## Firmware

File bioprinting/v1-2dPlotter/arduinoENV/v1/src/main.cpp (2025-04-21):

#include <Arduino.h>
#include <Wire.h>
#include <LiquidCrystal.h>
#include <Servo.h>

//JOYSTICK WIRES FACE RIGHT
//A is LEFTRIGHT
//B is UPDOWN
//GREEN IS UP
//BLUE IS DOWN
//GREEN IS LEFT
//BLUE IS RIGHT

//  Serial.print(digitalRead(A10)); returns 1 if joystick button is not pressed, returns 0 if it is pressed

const int joystickXPin = A8; // Left/Right
const int joystickYPin = A9; // Up/Down
const int joystickButtonPin = A10;

const int threshold = 50;

const int motorLeftRight1 = 2;
const int motorLeftRight2 = 3;
const int motorUpDown1 = 4;
const int motorUpDown2 = 5;

bool hasBeenPrinted = false; //is the print complete

bool isExtruding = false; //is the printer currently extruding bioink+cells

int currLocX = 0, currLocY = 0;

// const int vss = 53;   // Ground (LOW)
// const int vdd = 51;   // Power (HIGH)
// const int vo = 49;    // Contrast (PWM)
// const int rs = 47;    // Register Select
// const int rw = 45;    // Read/Write (set LOW for write)
// const int enable = 43; // Enable
// const int d4 = 33;    // Data line 4
// const int d5 = 31;    // Data line 5
// const int d6 = 29;    // Data line 6
// const int d7 = 27;    // Data line 7
// const int backlightA = 25; // Backlight anode (PWM-capable pin)
// const int backlightK = 23; // Backlight cathode

const int MSPerMMX = 85; //approx val for the amount of ms at 250/255 power it takes to move one mm X
const int MSPerMMY = 90; //approx val for the amount of ms at 250/255 power it takes to move one mm Y

//servo
const int extrusionServoDataPin = 46;

Servo extrusionServo;

int servoPos; //current servo position
const int extrusionServoInitPos = 75;
const int unitsPerLoopForExtrusionServoMovement = 1; //temp val, adj later

const int extrusionServoUpperLimit = 75;
const int extrusionServoBottomLimit = 115; //actually 120

//fan
const int fan5vPin = A13;
const int fanGNDPin = A14;

// LiquidCrystal lcd(rs, enable, d4, d5, d6, d7);

enum DIR {
  UP,
  DOWN,
  LEFT,
  RIGHT,
  STOPPED
};


String gcode[] = { //based on a 100mm^2 space, where toolhead is located at (0,0) at start; goal: draw a smiley face
  "G91", //relative positioning
  "G21", //units:mm

  "G0 X15 Y15", //smile

  "G1 E10", //start extruding

  "G0 X85 Y15", //end smile

  "G1 E0", //stop extruding

  "G0 X25 Y90", //start left eye

  "G1 E10", //start extruding

  "G0 X25 Y50", // end left eye

  "G1 E0", //stop extruding

  "G0 X75 Y90", //start right eye

  "G1 E10", //start extruding

  "G0 X75 Y50", //end right eye

  "G1 E0", //stop extruding

  "G0 X0 Y0" //home (could be g28 but i dont have switches)
};

void setup() {
  pinMode(motorLeftRight1, OUTPUT);
  pinMode(motorLeftRight2, OUTPUT);
  pinMode(motorUpDown1, OUTPUT);
  pinMode(motorUpDown2, OUTPUT);

  Serial.begin(9600);
  pinMode(joystickXPin, INPUT);
  pinMode(joystickYPin, INPUT);
  pinMode(joystickButtonPin, INPUT_PULLUP);

  Serial.println("Starting setup...");

  //servo
  pinMode(extrusionServoDataPin, OUTPUT);

  extrusionServo.attach(extrusionServoDataPin);
  extrusionServo.write(extrusionServoInitPos);

  servoPos = extrusionServoInitPos;

  //fan
  pinMode(fan5vPin, OUTPUT);
  pinMode(fanGNDPin, OUTPUT);
  digitalWrite(fanGNDPin, LOW);  // Set GND pin to LOW/GND

  // Serial.println("Configuring power pins...");
  // pinMode(vss, OUTPUT);
  // pinMode(vdd, OUTPUT);
  // pinMode(vo, OUTPUT);
  // pinMode(rw, OUTPUT);
  // pinMode(backlightA, OUTPUT); // Configure backlight anode pin
  // pinMode(backlightK, OUTPUT); // Configure backlight cathode pin

  // Serial.println("Setting power states...");
  // digitalWrite(vss, LOW);    // VSS to GND
  // digitalWrite(vdd, HIGH);   // VDD to 5V
  // digitalWrite(rw, LOW);     // RW to write mode
  // analogWrite(vo, 5);      // VO to ~50% contrast (PWM)
  // digitalWrite(backlightK, LOW); // Backlight cathode to GND
  // analogWrite(backlightA, 120);  // Backlight anode to 50% brightness
  // Serial.println("Power states set successfully.");

  // delay(1000);
  // Serial.println("Initializing LCD...");
  // lcd.begin(16, 2);
  // lcd.print("BioprinterV1!");
  // Serial.println("LCD initialized and message displayed.");

  Serial.println("10");
  delay(1000);
  Serial.println("9");
  delay(1000);
  Serial.println("8");
  delay(1000);
  Serial.println("7");
  delay(1000);
  Serial.println("6");
  delay(1000);
  Serial.println("5");
  delay(1000);
  Serial.println("4");
  delay(1000);
  Serial.println("3");
  delay(1000);
  Serial.println("2");
  delay(1000);
  Serial.println("1");
  delay(1000);
  Serial.println("Setup complete!");
}

bool joystickButtonIsPressed() {
  if (digitalRead(A10) == 1) {
    return false;
  } else if (digitalRead(A10) == 0) {
    return true;
  } else {
    Serial.println("Error: Unexpected joystick button state.");
    return true;
  }
}

void setPowerForGantry(DIR MOTOR_A_LEFT_RIGHT, DIR MOTOR_B_UP_DOWN) {
  if (MOTOR_A_LEFT_RIGHT == RIGHT && MOTOR_B_UP_DOWN == DOWN){
    digitalWrite(2,HIGH); //both blue
    analogWrite(5,250);
    digitalWrite(4,LOW);
    analogWrite(6,250);
  } else if (MOTOR_A_LEFT_RIGHT == LEFT && MOTOR_B_UP_DOWN == UP) {
    digitalWrite(2,LOW); //both green
    analogWrite(5,250);
    digitalWrite(4,HIGH);
    analogWrite(6,250);
  } else if (MOTOR_A_LEFT_RIGHT == LEFT && MOTOR_B_UP_DOWN == DOWN) {
    digitalWrite(2,LOW);//a green b blue
    analogWrite(5,250);
    digitalWrite(4,LOW);
    analogWrite(6,250);
  } else if (MOTOR_A_LEFT_RIGHT == RIGHT && MOTOR_B_UP_DOWN == UP) {
    digitalWrite(2,HIGH);//a blue and b green
    analogWrite(5,250);
    digitalWrite(4,HIGH);
    analogWrite(6,250);
  } else if (MOTOR_A_LEFT_RIGHT == LEFT && MOTOR_B_UP_DOWN == STOPPED) {
    digitalWrite(2,LOW); // Left only
    analogWrite(5,250);
    digitalWrite(4,LOW);
    analogWrite(6,0);
  } else if (MOTOR_A_LEFT_RIGHT == RIGHT && MOTOR_B_UP_DOWN == STOPPED) {
    digitalWrite(2,HIGH); // Right only
    analogWrite(5,250);
    digitalWrite(4,LOW);
    analogWrite(6,0);
  } else if (MOTOR_A_LEFT_RIGHT == STOPPED && MOTOR_B_UP_DOWN == UP) {
    digitalWrite(2,LOW); // Up only
    analogWrite(5,0);
    digitalWrite(4,HIGH);
    analogWrite(6,250);
  } else if (MOTOR_A_LEFT_RIGHT == STOPPED && MOTOR_B_UP_DOWN == DOWN) {
    digitalWrite(2,LOW); // Down only
    analogWrite(5,0);
    digitalWrite(4,LOW);
    analogWrite(6,250);
  } else if (MOTOR_A_LEFT_RIGHT == STOPPED && MOTOR_B_UP_DOWN == STOPPED) {
    analogWrite(5, 0); // Stop both motors
    analogWrite(6, 0);
  }
}

void controlGantry(int targetX, int targetY) {
  DIR xMovementDirection;

  if ((currLocX - targetX) < 0) { //dir is positive
    xMovementDirection = LEFT;
  } else if ((currLocX - targetX) == 0) { //already at loc
    xMovementDirection = STOPPED;
  } else if ((currLocX - targetX) > 0) { // dir is negative
    xMovementDirection = RIGHT;
  }

  int mmToMoveX = abs(currLocX - targetX);

  DIR yMovementDirection;

  if ((currLocY - targetY) > 0) { // dir is negative
    yMovementDirection = DOWN;
  } else if ((currLocY - targetY) == 0) { // already at loc
    yMovementDirection = STOPPED;
  } else if ((currLocY - targetY) < 0) { // dir is positive
    yMovementDirection = UP;
  }

  int mmToMoveY = abs(currLocY - targetY);

  //moves one motor at a time due to battery 
  
  int i = 0;

  for (int mmX = 1; (mmX <= (mmToMoveX) && hasBeenPrinted == false); mmX++) { //move one mm per loop until all mm movement is complete 
    setPowerForGantry(xMovementDirection, STOPPED);
    delay(MSPerMMX); //x moves slightly faster than y
    setPowerForGantry(STOPPED, STOPPED);
    Serial.print("moved1mmX \n");

    if (joystickButtonIsPressed() == true) { // abort print if joystick button is pressed
      Serial.println("Print job aborted!");
      // lcd.clear();
      // lcd.setCursor(0, 0);
      // lcd.print("Job Aborted!");
      hasBeenPrinted = true;
      return; //exit function
    }

    i++;

    if (i > 5) {
      i = 0;
    }

    //each loop, if it is extruding, turn the plunger down
    if (isExtruding == true && i == 5) {
      if (servoPos + unitsPerLoopForExtrusionServoMovement >= extrusionServoUpperLimit && servoPos + unitsPerLoopForExtrusionServoMovement <= extrusionServoBottomLimit) {
        extrusionServo.write(servoPos + unitsPerLoopForExtrusionServoMovement);
        servoPos = (servoPos + unitsPerLoopForExtrusionServoMovement);
        Serial.print("Moved extrusion servo to ");
        Serial.print(servoPos);
        Serial.print("\n");
      } else {
        Serial.println("Servo position out of bounds!");
      }
    }
  }

  i = 0;

  for (int mmY = 1; (mmY <= (mmToMoveY) && hasBeenPrinted == false); mmY++) { // move one mm per loop until all mm movement is complete
    setPowerForGantry(STOPPED, yMovementDirection);
    delay(MSPerMMY);
    setPowerForGantry(STOPPED, STOPPED);
    Serial.print("moved1mmY \n");

    if (joystickButtonIsPressed() == true) { // abort print if joystick button is pressed
      Serial.println("Print job aborted!");
      // lcd.clear();
      // lcd.setCursor(0, 0);
      // lcd.print("Job Aborted!");
      hasBeenPrinted = true;
      return; //exit function
    }

    i++;

    if (i>5) {
      i=1;
    }

    //each loop, if it is extruding, turn the plunger down
    if (isExtruding == true && i == 5) {
      if (servoPos + unitsPerLoopForExtrusionServoMovement >= extrusionServoUpperLimit && servoPos + unitsPerLoopForExtrusionServoMovement <= extrusionServoBottomLimit) {
        extrusionServo.write(servoPos + unitsPerLoopForExtrusionServoMovement);
        servoPos = (servoPos + unitsPerLoopForExtrusionServoMovement);
        Serial.print("Moved extrusion servo to ");
        Serial.print(servoPos);
        Serial.print("\n");
      } else {
        Serial.println("Servo position out of bounds!");
      }
    } else {
      Serial.print("Skipped extrusion");
    }
  }

  currLocX = targetX;
  currLocY = targetY;
}

void turnFanOn() {
  digitalWrite(fan5vPin, HIGH); // Set Power pin to HIGH/5V
}

void turnFanOff() {
  digitalWrite(fan5vPin, LOW); // Set Power pin to HIGH/5V
}

int j = 0;
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

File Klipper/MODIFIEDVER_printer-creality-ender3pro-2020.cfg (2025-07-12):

# This file contains pin mappings for the stock 2020 Creality Ender 3
# Pro with the 32-bit Creality 4.2.2 board. To use this config, during
# "make menuconfig" select the STM32F103 with a "28KiB bootloader" and
# serial (on USART1 PA10/PA9) communication.

# It should be noted that newer variations of this printer shipping in
# 2022 may have GD32F103 chips installed and not STM32F103. You may
# have to inspect the mainboard to ascertain which one you have. If it
# is the GD32F103 then please select Disable SWD at startup in the
# "make menuconfig" along with the same settings for STM32F103.

# If you prefer a direct serial connection, in "make menuconfig"
# select "Enable extra low-level configuration options" and select
# serial (on USART3 PB11/PB10), which is broken out on the 10 pin IDC
# cable used for the LCD module as follows:
# 3: Tx, 4: Rx, 9: GND, 10: VCC

# Flash this firmware by copying "out/klipper.bin" to a SD card and
# turning on the printer with the card inserted. The firmware
# filename must end in ".bin" and must not match the last filename
# that was flashed.

# See docs/Config_Reference.md for a description of parameters.

[stepper_x]
step_pin: PC2
dir_pin: PB9
enable_pin: !PC3
microsteps: 16
rotation_distance: 40
endstop_pin: ^PA5
position_endstop: 0
position_max: 235
homing_speed: 50

[stepper_y]
step_pin: PB8
dir_pin: PB7
enable_pin: !PC3
microsteps: 16
rotation_distance: 40
endstop_pin: ^PA6
position_endstop: 0
position_max: 235
homing_speed: 50

[stepper_z]
step_pin: PB6
dir_pin: !PB5
enable_pin: !PC3
microsteps: 16
rotation_distance: 8
endstop_pin: ^PA7
position_endstop: 0.0
position_max: 175 #CHANGED (200mm is physical limit, 175 gives enough reaction time to power off the printer if the limit doesn't work.)

[extruder]
max_extrude_only_distance: 100.0
step_pin: rpi:gpio27 #CHANGED to pi external motor driver
dir_pin: rpi:gpio22 #CHANGED to pi external motor driver
enable_pin: rpi:gpio17 #CHANGED to pi external motor driver
microsteps: 16
rotation_distance: 34.406
nozzle_diameter: 0.800 #CHANGED (0.830 is the physical orifice diameter, 0.800 is easier for slicers to handle, and the difference can be tuned out.)
filament_diameter: 1.750
heater_pin: PA1
sensor_type: EPCOS 100K B57560G104F
sensor_pin: PC5
control: pid
# tuned for stock hardware with 200 degree Celsius target
pid_Kp: 21.527
pid_Ki: 1.063
pid_Kd: 108.982
min_temp: 0
max_temp: 250
min_extrude_temp: 0 #NEW LINE: allows cold extrusion

[heater_bed]
heater_pin: PA2
sensor_type: EPCOS 100K B57560G104F
sensor_pin: PC4
control: pid
# tuned for stock hardware with 50 degree Celsius target
pid_Kp: 54.027
pid_Ki: 0.770
pid_Kd: 948.182
min_temp: 0
max_temp: 130

[fan]
pin: PA0

[mcu]
serial: /dev/serial/by-id/usb-1a86_USB_Serial-if00-port0
restart_method: command

[printer]
kinematics: cartesian
max_velocity: 300
max_accel: 3000
max_z_velocity: 5
max_z_accel: 100

# Pin mappings for BL_T port
#[bltouch]
#sensor_pin: ^PB1
#control_pin: PB0

[display]
lcd_type: st7920
cs_pin: PB12
sclk_pin: PB13
sid_pin: PB15
encoder_pins: ^PB14, ^PB10
click_pin: ^!PB2

[include mainsail.cfg] #ADDED

[mcu rpi] #ADDED
serial: /tmp/klipper_host_mcu

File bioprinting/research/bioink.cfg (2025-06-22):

[general]
name = "Bioink Configuration"
description = "Configuration file for bioprinting research project. This file defines the materials, printing parameters, and post-processing steps for the bioink used in 3D bioprinting, along with the specific components, their properties, and an explanation of why they are used and how they work."

[materials]
type = "bioink"
components = ["Sodium Alginate (2% w/v)", "Calcium Chloride (100 mM)", "Chlorella Vulgaris (~1×10^7 cells/mL)"]
properties = {
    "Sodium Alginate": {
        "function": "Provides gel-like consistency and biocompatibility",
        "mechanism": "Forms hydrogels upon crosslinking with calcium ions, allowing for cell encapsulation and structural integrity."
    },
    "Calcium Chloride": {
        "function": "Crosslinking agent",
        "mechanism": "Facilitates the formation of stable hydrogels by interacting with sodium alginate, enhancing mechanical properties."
    },
    "Chlorella Vulgaris": {
        "function": "Bioactive component",
        "mechanism": "A form of algae that provides the living component to the bioink."
    }
    "Water": {
        "function": "Solvent",
        "mechanism": "Dissolves the sodium alginate and facilitates the mixing of components."
    }
}

[custom_printing_parameters]
extruder_temperature = 0 # not heated extruder
nozzle_diameter = 0.8 # mm
bed_temperature = 25
speed = 5 # mm/s
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

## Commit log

2025-04-13 got motion working - waiting on the print
2025-04-15 First sucsessful drawing
    Connected a sharpie and drew a smiley face.
    TODO: Servo to control extruder height?
    Figure out bioink, cell type, etc
2025-04-19 gcode working for X/Y, cadded models to allow for Extrusion, printing now
    TODO: add code for extrusion, confirm hardware for extrusion, add z axis, etc
    [Custom Servo Horn.stl, Custom Servo Horn2.stl, pen_holder1v2.stl, pen_holder2.3mf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]
2025-04-20 built the physical extrusion mechanism
    added the timelapse for the third print job, as the second wasn't saved by the printer properly and the first is already included. Now working on the programming aspect for the extrusion, then will w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
    [pen_holder2.3mf]
2025-04-20 added print abortion via joystick button
2025-04-20 turning off for the night; saving code to github
    - started work on the servos
    - need to make a basic file to find servo upright and bottom pos, and implement
2025-04-20 added additional media (photos) for use later of the prototypes
2025-04-20 redesigned the attachment mount again and started the print
    after testing the servo's range of motion, it had to be moved to work properly, resulting in a change in the mount to change the position of the servo. The holes were also incorrectly spaced on the o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
    [pen_holder2v3.3mf, pen_holder2v3.stl]
2025-04-20 print jobs 4 & 5 had bed adhesion issues, printing 6 with modifications now
    - lowered print speed
    - switched from textured plate to supertack
    - switched from pla to petg
    [pen_holder2v3.3mf]
2025-04-21 extrusion works but servo is too weak to move the plunger
2025-04-24 started a expenses excel
    [expenses.csv]
2025-04-26 stopping working on the project till summer
    [Bioextruder_Final.stl, Gears.stl, Plunger.stl, Printhead_Final.stl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]
2025-04-28 bought an ender 3 pro and a pi 5 8gb ram
    [expenses.csv]
2025-04-29 yesterday, set up the pi server and got it online. today, i set up the ender and printed a benchy. this commit adds media
    [Printhead_Final.3mf]
2025-05-01 worked on a new design
    [BLT_Holder.stl, Body.stl, Clamp.stl, Guide.stl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]
2025-05-03 finalized v2.1 design and started the pc half of printing
    The model is split into two halves: screws, holders, etc in PLA, and the main holder and parts in PC. Will update on how PC print goes. Will print PLA tomm.
    [1xM3x10mmThreadedRod.3mf, 1xM3x8mmThreadedRod.3mf, 1xM4x6mmThreadedRod.3mf, 1xM5x10mmThreadedRod.3mf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]
2025-05-03 adjusted brim settings
    pc had good first layer, but severe warping by layer 5 (4mm off plate)
    changed brimobj gap to 0, adj brim from 5mm to 25mm
    praying for better second try
2025-05-03 started v3 of pc
    print job 2 also lost adhesion and failed, but it lasted ~30-40 layers instead of five. currently reprinting with gluestick and increased ambient chamber temp (let heat for longer, added towel), and 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
    [Display_Cover_ender3pro.stl]
2025-05-04 pc woked on the third try. printing grears etc in pla rn
    - added timelapse of pc
    - edited the main file because due to the polycarbonate the pla had bad layer adhesion, so i made changes to account for that
2025-05-05 pla gears printed fine, curr. mid assembly of bioextruder
    waiting on a an m8 threaded rod and bolt from amazon. everything else is printed and works
2025-05-10 amazon parts arrived, working on assembly
    Redesigned the plunger in blender to work with the new syringes. The invoice from amazon is in the media folder
    [plunger.blend, plunger1.stl]
2025-05-10 finished assembly
    TODO/Timeline:
    Pi-Klipper-test (only tested manually so far)
    make a cad model to attach assembly to printer
    custom cura settings and make a test print with no ink (empty chamber)
    buy bioink supplies and make a test print with food dye, sodium alginate, and calcium cloride
    buy algae and test print with algae
    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
2025-05-10 redesigned mounting system
    prototype printing now (PETG). This is to connect the assembly to the gantry
    [hot_end_holder.blend, hot_end_holder_redesigned.stl]
2025-05-10 added plunger timelapses from the assembly v1 stage
2025-05-12 added timelapse of yesterdays print used in this morings progress
    since i snapped the pc version of this part (the thing that the wheels and lever screw into, the thing that the main body clipps into) that i printed before, i reprinted it in petg and it works fine
2025-05-13 Redesigned and printed the OG hot end holder so that i can swap that out of need be
    [hot_end_holder_og.blend, hot_end_holder_og_redesigned.stl]
2025-05-13 yesterday redesign didn't work, redesigned again, printing now
    added yesterdays timelapse, stl of new one, and blender files for new one
    [hot_end_holder_og.blend, hot_end_holder_og_redesigned_v2.stl]
2025-05-13 second redesign worked, bioprinter now has two toolhead options, bioprinter and FFF/FDM
    To use FDM, unplug and remove bioprinter, place in notch, flip lever, and plug in PTFE tube and extruder motor. Then change firmware to standard ender and all set
    To use Bioprinter, unplug PTFE tube and extruder motor, remove FDM, place bioprinter in notch, flip lever, plug in motor and change firmware.
2025-06-19 started a plan for moving forward, updated expenses CSV, stared working on a klipper profile
    [expenses.csv]
2025-06-21 cont. working on the plan, klipper installation and customization of printer .cfg file
2025-07-12 the following is three days worth of testing that has been so frantic that i have'nt had time to commit (15+hours) tldr; flashed klipper, fixed burnt motor driver
2025-07-14 I love html in md (tldr; motion works, next step: gelatin)
    [cube_sliced_bioprinter.3mf]
2025-07-15 gelatin day 1 ?
    [intestinal_wall_tissue.3mf]
2025-07-16 finished gelatin stage - this commit is for media, writeup/journal comes later
